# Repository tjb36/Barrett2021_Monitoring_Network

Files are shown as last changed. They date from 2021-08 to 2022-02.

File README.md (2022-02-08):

# "An Environmental Monitoring Network for Quantum Gas Experiments and Devices"

The purpose of this repository is to make available the data and code used in the study *"An Environmental Monitoring Network for Quantum Gas Experiments and Devices"*, by T. Barrett, et al. The publication is available [here](https://doi.org/10.1088/2058-9565/ac3385).

The system was designed for monitoring a suite of ultracold atom experiments, together with a variety of relevant environmental conditions to which the experiments are extremely sensitive. Approximately ~100 sensors are installed onto the network, and the data is consolidated into a standardised format in a time-series database. All data is available to inspect remotely for end users through custom dashboards. A high level schematic of the system looks like the following:



The code in this repository is organsied according to several main blocks in the system:

1) Environmental measurements are collected using various transducers (photodiodes, thermocouples, current sensors, etc). There are multiple of these "nodes" located around the buliding, connected to an isolated internal local area network using ethernet cables. These microcontrollers are usually Arduino-based, because they are small, cheap, and quick to set up and can be learned by any users in the lab with little programming experience. Examples of firmware deployed on these devices can be found at /Microprocessors Firmware/Sensor Node Devices/. Several transducers will typically be interfaced using the same microcontroller - for example, the board detailed at /Electronics/Photodiode and Thermocouple Amplifier/ allows x12 photodiodes and x8 thermocouples to be measured in succession by a single microcontroller node (gerbers/drill manufacture files are provided).

2) After a set time interval (typically every 20 seconds), a "Collector" microprocessor will poll all the node microcontrollers around the building, requesting that they take sensor readings and send back the values via the network. The firmware for this device can be found at /Microprocessors Firmware/Firmware_Collector.ino. This device keeps track of whether a reply was received from each device (to allow alerts to be sent out if a device becomes inactive), and sends the data as they arrive via serial USB connection to a "Parser" device, based on a Raspberry Pi.

3) The python script running on the Raspberry Pi can be found at /Parser Script/MapCollectorValuesToInfluxDB.py. The Raspberry Pi acts as the single points of contact with the outside internet, and the USB serial acts as a bridge between the internal LAN and the external internet (to avoid connecting many individual microcontrollers to the internet, and allow clearer separation). This script receives the data from the Collector via USB, performs a series of checks on the integrity of the data, and then extracts the relevant values from the payload. The script adds tags, and performs conversion from ADC counts to sensor values, for example (using calibration constants), and finally sends the data via HTTP to the InfluxDB database for storage.

4) An InfluxDB instance needs to be set up at a location that is accessible by the Raspberry Pi, and by default listens on port 8086. InfluxDB can be installed according to the developer's website https://portal.influxdata.com/downloads/ (a docker image is available to make installation quick and simple). In our setup, a virtual machine (VM) provisioned by the university hosts the InfluxDB instance, with 1TB of backed-up disk space (although the amount of data accumulated is typically only several GB per year).

5) For data visualisation, a Grafana instance must be set up, which can be done according the developer's website https://grafana.com/grafana/download?pg=get&plcmt=selfmanaged-box1-cta1 (similarly to InfluxDB, a docker image is available for easy installation). The Grafana instance must then be pointed to the InfluxDB location (in our setup, both Grafana and InfluxDB run on the same virtual machine). Custom dashboards should then be created in Grafana, and data be accessed by individual users as needed.

Typical examples of dashboards are shown below:

Dashboards

which are displayed on various screens around the labs:



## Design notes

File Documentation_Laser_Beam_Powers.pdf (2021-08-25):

## QSD Monitoring Network

## Measuring Laser Beam Powers

T. Barrett

July 2018

### Measuring Laser Beam Powers

Laser beam power is measured with a photodiode - a device which produces electron-hole pairs when photons of sufficient energy fall on the depletion region of the p-n junction semiconductor. Because there is a separation of charge either side of the depletion region, there is also an internal electric field across it. Therefore, when light falls on the active area the electrons move towards the cathode and holes towards the anode, leading the generation of an electrical photocurrent. To convert the photocurrent into a measurable voltage signal, a transimpedance amplifier can be used, shown schematically in Fig. 1.

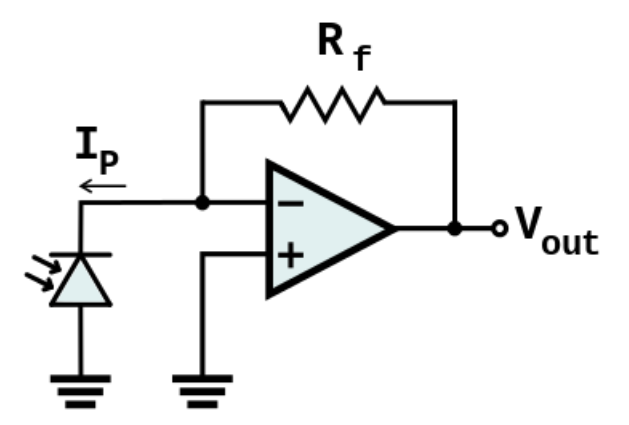
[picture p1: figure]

FIGURE 1: Schematic of a photodiode connected in photovoltaic mode with a transimpedance amplifier configuration, which gives an output voltage proportional to
the incident light power that can be scaled using the feedback resistor.

Photodiodes can be operated in either of two modes: photoconductive (with an external reverse bias applied across it), or photovoltaic (with zero bias across it). In general, photovoltaic mode reduces dark current, but is less optimal for bandwidth and response time. An excellent source of information on photodiode circuits and configurations is the book Photodiode Amplifiers - Op Amp Solutions, by J. Graeme [1]. In the particular application described in this document bandwidth is not a priority, and the photovoltaic arrangement is employed as shown in Fig. 1. Here, the op amp acts to make both its inputs equal to each other, which is zero volts due the non-inverting input being explicitly grounded. Since the photocurrent Ip is forced to flow through the feedback resistor Rf
, the voltage drop across this resistor is

∆V pVout 0q Ip -
Rf
, | (1)

and so the output voltage Vout is simply linear with the photocurrent. The amount of photocurrent generated is also linear with incident optical power through a factor known as the responsivity (measured in AW1
), and so this configuration provides a measurable output voltage that is linear with laser light power, which can be conveniently scaled by changing the gain of the transimpedance amplifier using the feedback resistor.
It was decided to use the Thorlabs FDS100, shown in Fig. 2 a), which is a standard silicon photodiode with a large active area of 13 mm²
, and costing £10 each. The responsivity at 780 nm
is 0.5 AW1
, as can be seen in Fig. 2 b). For the transimpedance op amp, the MCP604X series from Microchip is used, which is available with either one, two, or four op amps in a single chip. This is a low power op amp, designed for battery powered applications. It has a relatively low bandwidth, but this isn’t an

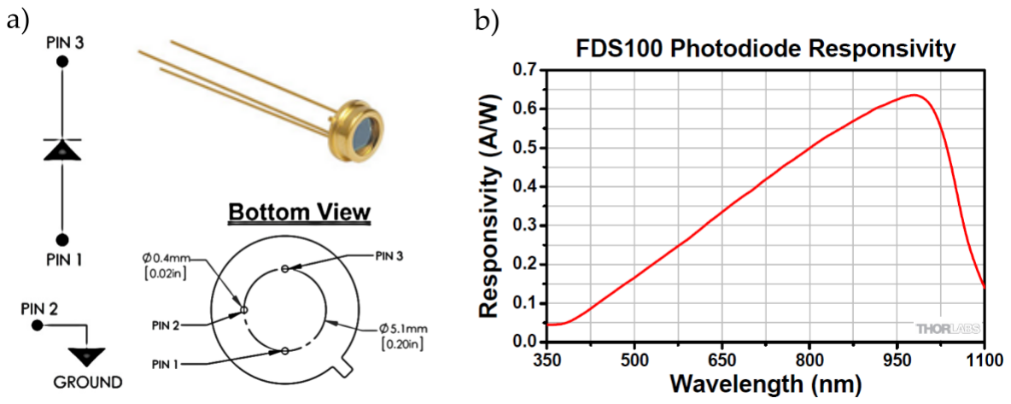
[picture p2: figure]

FIGURE 2: Thorlabs FDS100 Photodiode. a) Photograph and pin connections. b) Responsivity of the diode as a function of wavelength.

issue here. The main reason for using this op amp is that it is a single-supply rail-to-rail type, which means that its output voltage can get very close (to within 10 mV) of the power supply rails, in contrast to regular op amps which typically have a headroom of 1 V or more. This means that if the op amp is powered with 0 V (VSS) and +5 V (VDD), then its output signal will be able to get very close to +5 V, but not any higher. This is important because it provides a convenient way to protect the analog input pins of the Arduino microcontroller.
To be able to mount the FDS100 photodiodes and allow them to be integrated easily into the setup on the optical tables, several components were purchased from Thorlabs, as shown in Fig. 3. An 8 mm circular hole is drilled into the centre of a 1 inch SM1CP2 threaded cap, and the photodiode is then attached using a hot glue gun. This threaded cap then screws into a SMR1/M lens mount, which allows a neutral density filter to be attached if necessary (for example, NE01A-B. Everything can then be mounted to the optical table using standard posts. The photodiode is connected to wires using a removable socket with solder tail (STO5S).

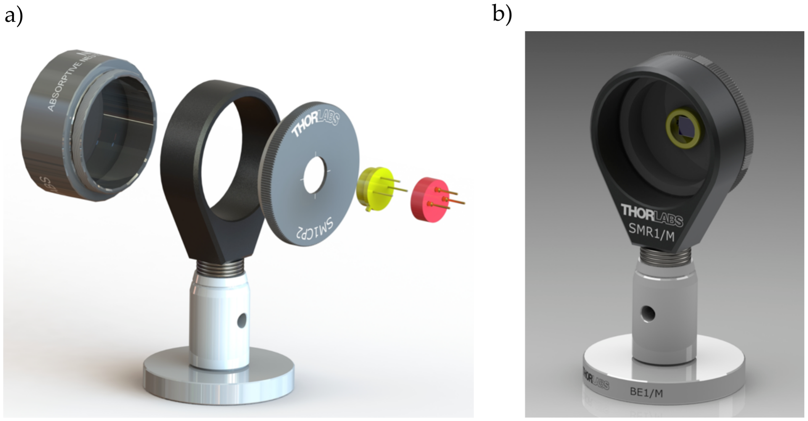
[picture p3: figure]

FIGURE 3: Exploded view a) and fully assembly b) photodiode with standard Thorlabs components.

For testing, the circuit was assembled and the output voltage was measured as a function of the incident laser light power, having a wavelength of 780 nm, with the results displayed in Fig.
4. Three different ranges with maximum powers of 100 µW, 1 mW, and 10 mW were achieved by inserting appropriate values of Rf
, and are shown in (a), (b), and (c), respectively. In this case, the op amp was powered with 0 VÑ+3.3 V. It can be seen that the output voltage is nicely linear with input light power, and never exceeds +3.3 V, meaning that the microcontroller will be safe.

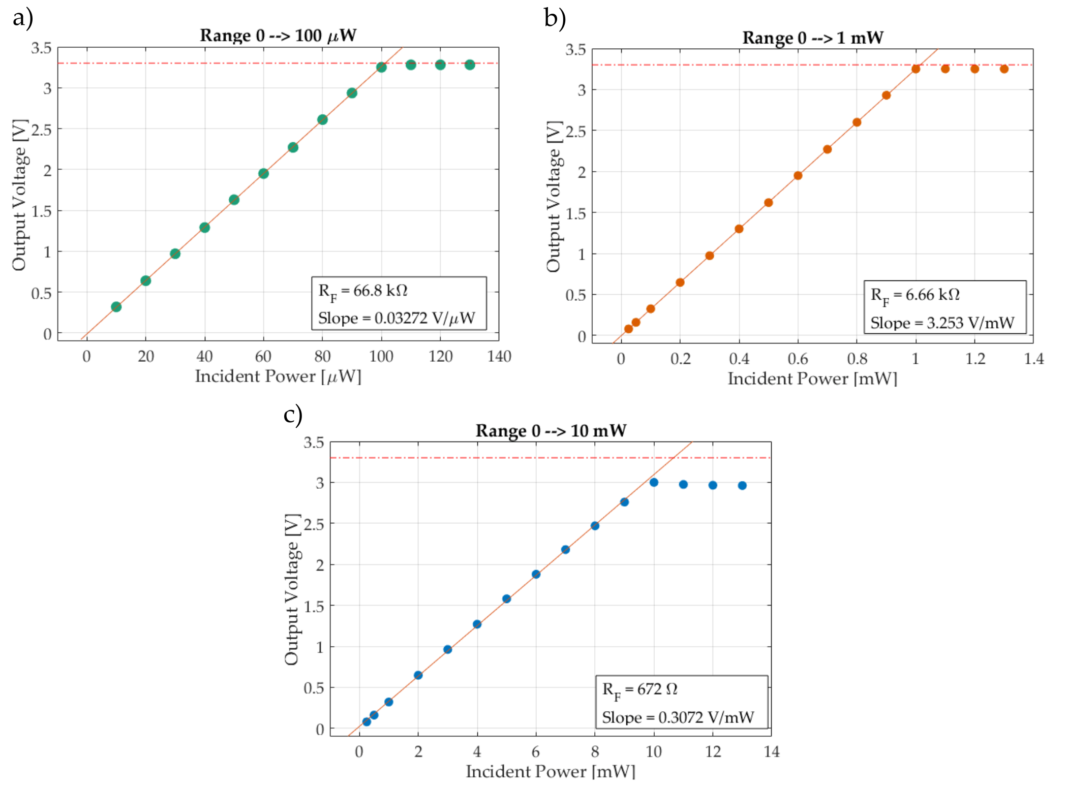
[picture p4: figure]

FIGURE 4: Measurements of the output voltage signal from a photodiode with a transimpedance amplifier as a function of incident laser light power. Three different ranges are shown in a), b) and c), corresponding to feedback resistors of 66.8 kΩ, 6.66 kΩ, and 672 Ω, respectively.

Arduino Code

The analog voltages can be read very easily using the following code, which reads x6 inputs. The ADC resolution is 10-bit on most Arduinos, giving possible values from 0 to 1023 as outputs from the analogRead() function.

1 /*

02 Mul tipleAnalogVol tageReadr
2 * Code f o r measuring mul tiple analog v ol t a g e s . 3 */
4
5 // Analog inpu t channel sen so r ADC v alue s
6 unsigned i n t sensorValueA0 = 0 ;
7 unsigned i n t sensorValueA1 = 0 ;
8 unsigned i n t sensorValueA2 = 0 ;
9 unsigned i n t sensorValueA3 = 0 ; 10 unsigned i n t sensorValueA4 = 0 ; 11 unsigned i n t sensorValueA5 = 0 ; 12 S t ri n g p aylo ad S t r ;
13
14 void se tup ( ) {
15 S e r i a l . begin ( 9 6 0 0 ) ; 16 }
17
18 void loop ( ) {
19
20 | sensorValueA0 = analogRead (A0 ) ;
21 | sensorValueA1 = analogRead (A1 ) ;
22 | sensorValueA2 = analogRead (A2 ) ;
23 | sensorValueA3 = analogRead (A3 ) ;
24 | sensorValueA4 = analogRead (A4 ) ;
25 | sensorValueA5 = analogRead (A5 ) ;
26 | p aylo ad S t r = ”” ;
27 | p aylo ad S t r = p aylo ad S t r + sensorValueA0 + ” , ” + sensorValueA1
28 | + ” , ” + sensorValueA2 + ” , ” + sensorValueA3 + ” , ”
29 | + sensorValueA4 + ” , ” + sensorValueA5 ;
30
31 | S e r i a l . p ri n t ( ”Analog Vol t age s : ” ) ;
32 | S e r i a l . p ri n tl n ( p aylo ad S t r ) ;
33 | delay ( 1 0 0 0 ) ;
34 }

The output from the Serial Monitor is shown in Fig. 5.

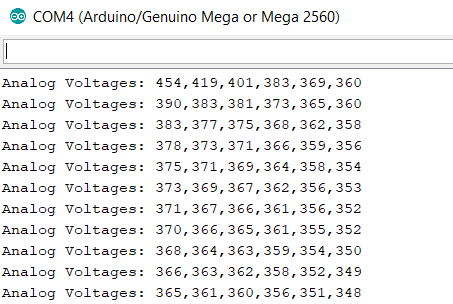
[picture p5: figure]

FIGURE 5: Serial Monitor output from reading multiple analog voltages.

### 1 References

[1] J. Graeme. Photodiode Amplifiers - Op Amp Solutions. McGraw-Hill Education, 1995.

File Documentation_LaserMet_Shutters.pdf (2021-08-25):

## QSD Monitoring Network

## Measuring LaserMet Shutter States

T. Barrett

July 2018

### Measuring LaserMet Shutter States

At the output of each of the 20 m seed fibres around the labs, as well as in front of every laser, is an LS10-12 LaserMet safety laser beam shutter, capable of blocking several watts of optical power. These shutters are connected to a safety interlock system, and when the interlock goes into a tripped state (for example, when lab door is left open for too long) the shutter power is removed and the flag falls down under gravity, blocking the beam. It is useful to be able to monitor the states of these shutters around the building, to know exactly where there is laser light present in the line at any one time.

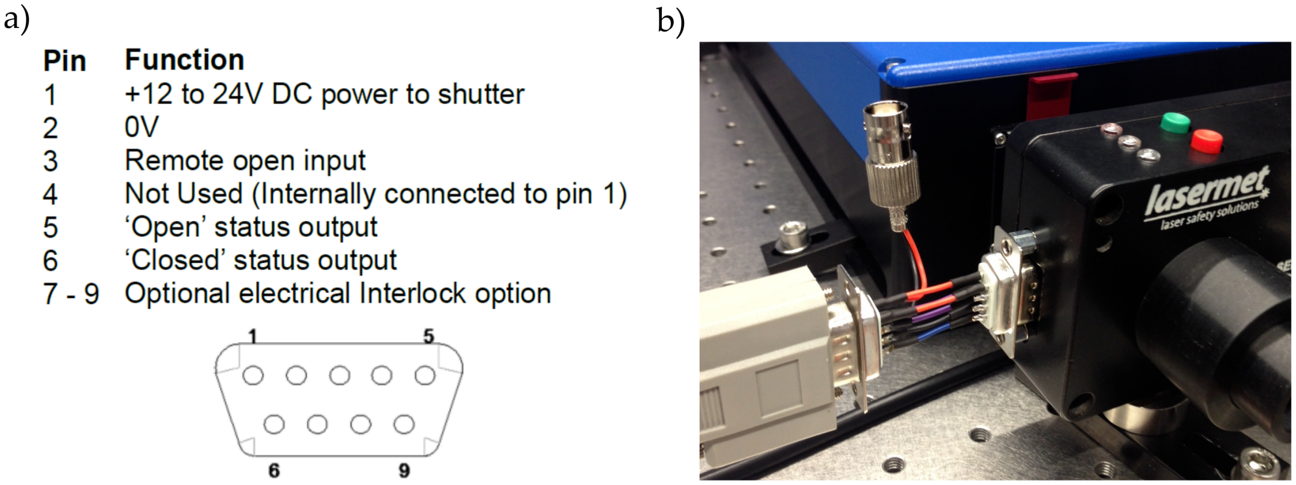
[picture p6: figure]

FIGURE 1: Remote monitoring of the LaserMet shutter states. a) Pin allocations for the 9-pin subD connector. b) An in-line adapter to connect the ’Open status output’
pin to an external device via BNC cable.

The shutter is mounted on the optical bench and interfaced with a 9-pin subD cable, as can be seen in Fig. 1 b). Page 3 of the LS10-12 user manual shows that there is a ’Open status output’ on pin 5 of the subD, with the pin allocations given in Fig. 1 a). When the shutter is opened (which is indicated by the red light on top of the shutter switching on), then the power supply of the system, which is +22 V in this case, is sent to pin 5. This signal allows remote monitoring of the shutter state.
In order to get access to this ’open status output’ pin, we made some adapters which go in-line with the shutter, connecting the centre pin of a BNC cable to pin 5, and the shield of a BNC to ground on pin 2. The adapter is shown after installation in Fig. 1 b). When the shutter is open, the centre pin of the BNC will get +22 V with respect to the outer shield. This allows access to the ’open’ indicator signal, whilst avoiding having to cut into the existing cable, and the adapter can simply be plugged in.
One problem is that the shutter ’open status’ pin receives +22 V, which is too high for the Arduino digital input pins, which are tolerant only up to +5 V on most models (and only to +3.3 V on the Due). Therefore, to convert the higher voltages into lower ones, an optocoupler circuit was designed, and is shown schematically in Fig. 2 a). The optocoupler used is the Vishay VO2630, which is a dual channel version - allowing two shutters to be interfaced with the same circuit. The datasheet states that a minimum of 5 mA is needed to turn on the input side LEDs, and so a 4 kΩ resistor is placed in series with the input from the shutter, to allow this current to flow. The output sides of the optocoupler then connect to two spare digital input pins on the Arduino microcontroller. The truth table in the VO2630 datasheet (page 3) shows that there is an inversion of the logic - i.e. when the input is high, the output is pulled low. Therefore, in the Arduino sketch, when an input LOW level is detected, this is interpreted as a ’shutter open’ signal, and vice versa. The 4 kΩ pull-up resistors on the output side ensure that the digital input pins remain HIGH when the shutters are closed and the optocoupler LEDs are off. This HIGH level voltage is now only +5 V, which is safe to pass to the microcontroller digital input pins. The whole circuit was made into a compact PCB, with two independent channels, a 3D view of which is shown in Fig. 2 b).

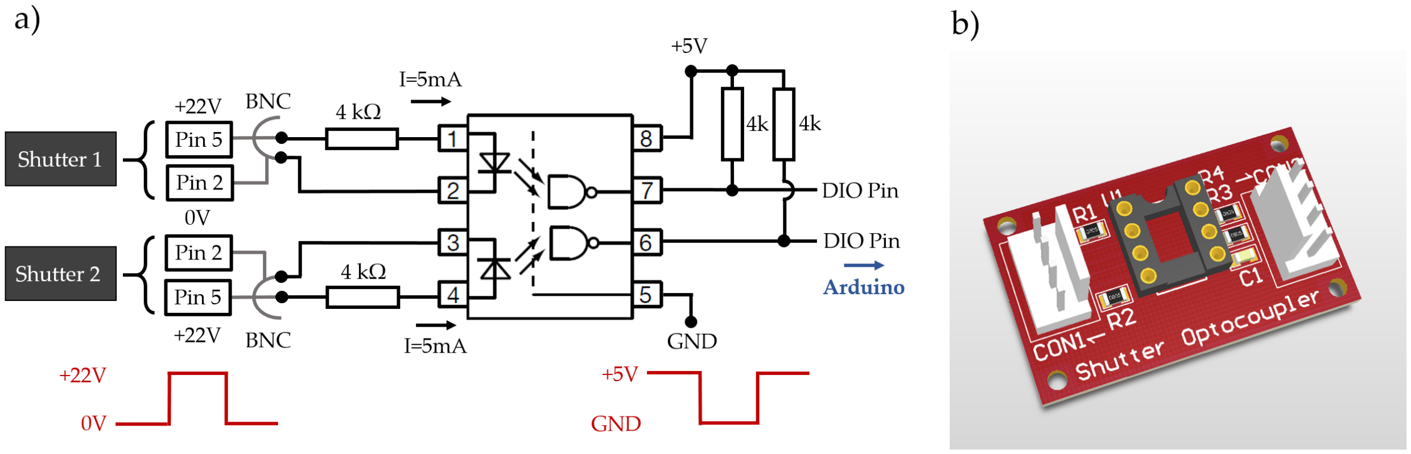
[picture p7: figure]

FIGURE 2: a) Schematic of the ’Shutter Optocoupler’ circuit. The circuit takes the +22 V signal output from the LaserMet shutters when they are open, and converts it down to +5 V, which can be safely read by an Arduino microcontroller’s digital input pins. b) A 3D view of the small PCB, made to facilitate two independent conversion channels, for two shutters in the lab.

Arduino Code

1 /*

04 L ase rMe tShu t te rRe ade r
2 | Code f o r reading in the s t a t e s o f two LaserMet s h u t t e r s
3
4 */
5
6 c on s t i n t Pi n S h u t t e r 1 = 2 ; 7 c on s t i n t Pi n S h u t t e r 2 = 3 ; 8 i n t S h u t t e r S t a t e 1 = 0 ;
9 i n t S h u t t e r S t a t e 2 = 0 ;
10
11 void se tup ( ) {
12
13 | S e r i a l . begin ( 9 6 0 0 ) ;
14 | pinMode ( Pi n S h u t t e r 1 , INPUT) ;
15 | pinMode ( Pi n S h u t t e r 2 , INPUT) ;
16
17 }
18
19 void loop ( ) {
20
21 | i f ( di gi t alR e a d ( Pi n S h u t t e r 1 ) == HIGH) {
22 | S h u t t e r S t a t e 1 = 0 ;
23 | } el s e {
24 | S h u t t e r S t a t e 1 = 1 ;
25 | }
26
27 | i f ( di gi t alR e a d ( Pi n S h u t t e r 2 ) == HIGH) {
28 | S h u t t e r S t a t e 2 = 0 ;
29 | } el s e {
30 | S h u t t e r S t a t e 2 = 1 ;
31 | }
32
33 | S e r i a l . p ri n t ( ” S h u t t e r 1 S t a t e = ” )
34 | S e r i a l . p ri n t ( S h u t t e r S t a t e 1 )
35 | S e r i a l . p ri n t ( ” , S h u t t e r 2 S t a t e = ” )
36 | S e r i a l . p ri n tl n ( S h u t t e r S t a t e 2 )
37
38 delay ( 1 0 0 0 )
39
40 }

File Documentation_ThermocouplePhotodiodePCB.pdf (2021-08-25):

# QSD Monitoring Network

# Multiple Thermocouple and Photodiode PCB

# T. Barrett

# July 2018

# Multiple Thermocouple and Photodiode PCB

In most cases, we will want to read in several thermocouples and photodiodes signals from different sources, all from the same microcontroller. For the temperatures, many of the MAX31855K

# breakout boards could be connected together. However, for a neater solution, custom PCBs

were designed and assembled, as in Fig. 1. Each PCB allows x12 photodiodes, and x8 thermocouples. The latter makes the board useful when performing a vacuum bakeout, for example, when many locations on the chamber need to be simultaneously measured.

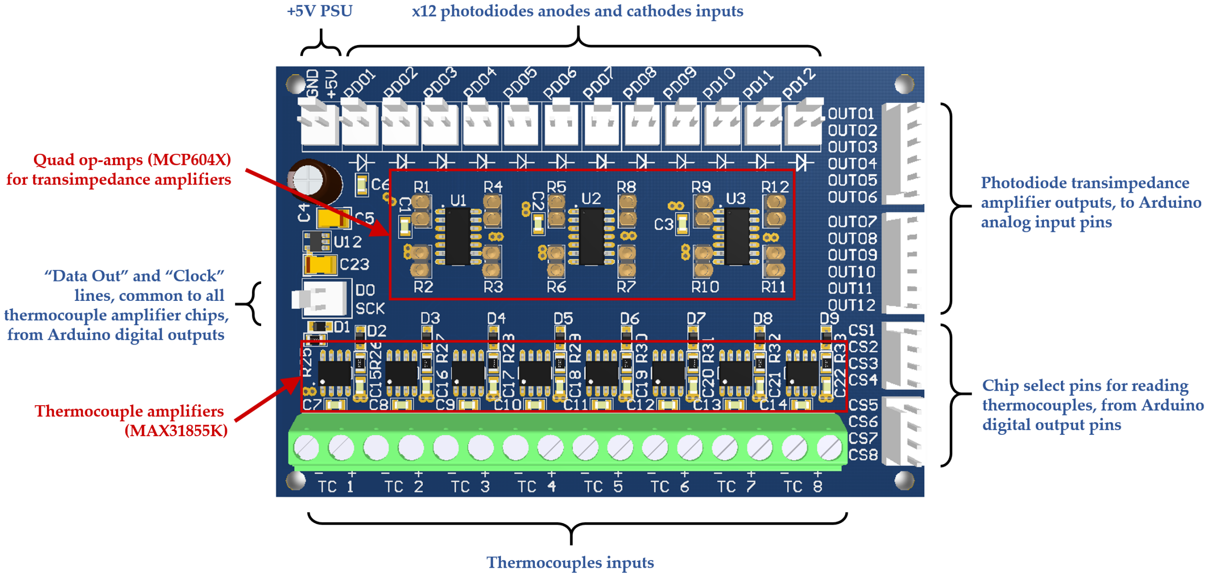
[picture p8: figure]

# FIGURE 1: PCB for reading multiple temperatures and laser powers. The board allows

x8 thermocouples and x12 photodiodes to be read.

# The design is based on the MAX31855K breakout board, and incorporates independent am-

plifier chips - one per thermocouple. However, there is only a single +3.3 V regulator (LP2981-
N) shared amongst all chips, along with a single set of decoupling power supply capacitors. All

# amplifiers also share common ’Data Out’ (DO) and ’Clock’ (SCK) lines, reducing the number

of digital output pins required. Each amplifier chip still requires its own dedicated ’Chip Se-lect’ (CS) pin, which indicates to each one that it’s time to read data. All thermocouple headers have 10nF capacitors across the terminals to reduce noise, as well as the digital pins having a resistor-diode combination to make the pins both 5 V and 3.3 V tolerant, for compatibility with different microcontrollers.
For the photodiodes, the PCB includes x3 MCP6044 op amps, which are quad versions,

# and therefore allows x12 photodiodes to be amplified. The op amps are configured in tran-

simpedance configuration, as described in the documentation Measuring Laser Beam Powers, and have sockets for through-hole axial resistors to be swapped out easily for changing the amplifier gains.

# Multiple Thermocouple and Photodiode PCB Schematics

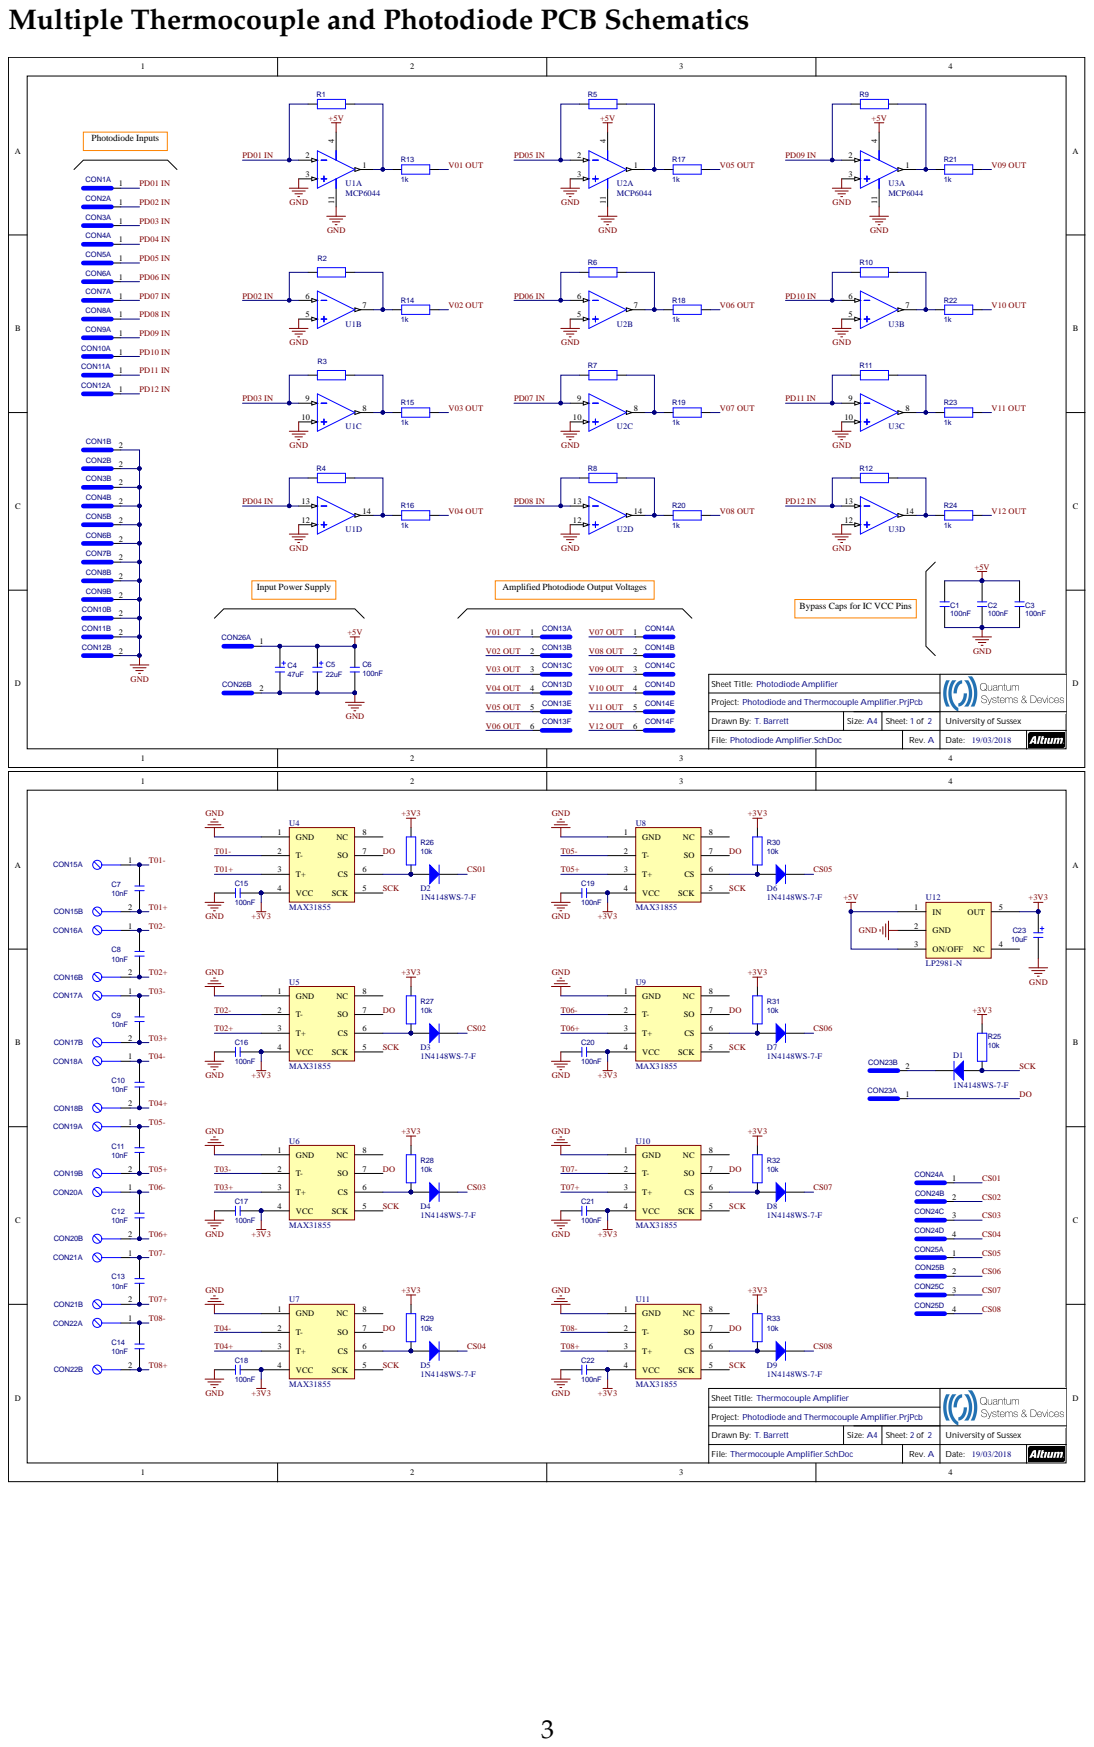
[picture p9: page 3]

Amplified Photodiode Output Voltages

Bypass Caps for IC VCC Pins

Project: Photodiode and Thermocouple Amplifier.PrjPcb

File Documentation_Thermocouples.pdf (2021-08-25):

## QSD Monitoring Network

## Measuring Temperatures

T. Barrett

July 2018

### Measuring Temperatures

For sensing temperatures in the lab, it was decided to use thermocouples, since they are cheap, reliable, and allow a high range of temperatures to measured. This means that the same system can be used when baking out a vacuum chamber, which typically means reaching temperatures of up to 200 C. Specifically, the most common thermocouple is the K-type, which has a range of around (200 C Ñ 1250 C).

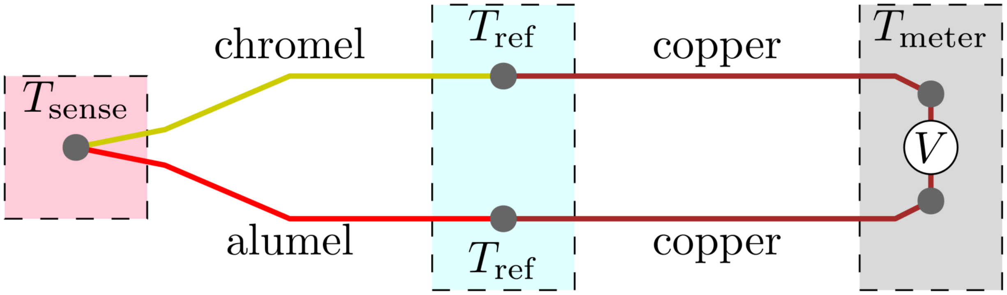
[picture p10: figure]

FIGURE 1: Schematic of a thermocouple. Two different metals are joined and positioned at the region to be sensed, Tsense. By knowing the temperature at the reference point, Tref, the absolute temperature can be determined by appropriate conversion of
the voltage, V . Image taken from [1]

A thermocouple, shown schematically in Fig. 1, relies on the Seebeck Effect, which describes the appearance of temperature-dependent voltage at the junction of two wires of different metals, converting thermal energy into electrical energy. For the K-type thermocouples, the positive lead is usually chromel (90% nickel, 10% chromium), and the negative lead alumel (95% nickel, 2% aluminium, 2% magnesium, 1% silicon). The voltage produced is very small (typically 1 mV at room temperature, with a sensitivity of 41 µV C

1
) and so must be amplified to a measurable value. In addition, the voltage must be linearised, along with being corrected for the cold-junction temperature. This is because the thermocouple is a differential device and so must be compensated with a reference junction of known temperature, in order to obtain an absolute value.

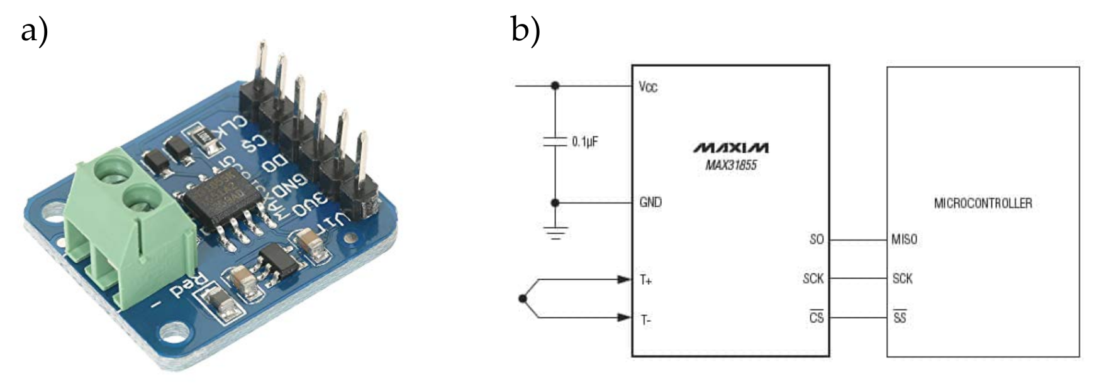
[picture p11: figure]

FIGURE 2: a) Adafruit MAX31855K assembled breakout board and b) connections schematic to the chip itself.

A convenient integrated circuit (IC) chip to use for this purpose is the MAX31855K from Maxim, which is optimised specifically for the K-type thermocouple, and whose schematic is shown in Fig. 2 b). This chip performs cold-junction compensation by measuring its internal temperature acting as a reference, in addition to the hot junction. Subsequently, the chip also converts the thermocouple voltage into a 14-bit digital signal ready for readout by using an on-board analog-to-digital converter (ADC), and so doesn’t require any analog inputs to work. The chip allows the temperature to be read out with a resolution of 0.25 C, and exhibits and accuracy of 2

C. Note in the datasheet that this IC has a typical conversion time of 70 ms, during which time the cold and hot junction voltages are converted, along with some fault detection being performed. In practice, this limits the frequency with which temperatures can be measured to 10 Hz, as one needs to wait at least until the conversion has finished before the next value can be read.
Communication with the IC (slave) is achieved using the serial peripheral interface (SPI) protocol, which requires connections to three digital I/O pins on an external microcontroller (master). The signals required are:
- SCK - serial clock - provides timing synchronisation between devices, and indicates when the next bit of data should be presented.
- SS (or CS) - slave select (or chip select) - typically pulled low by the master to indicate to the slave that it’s time to read data.
- MISO - master in slave out - contains each bit of data sent from the slave to the master.

The MAX31855K can be purchased already on a breakout board (for example, from Adafruit here: www.adafruit.com/product/269), which already has the necessary 3.3 V regulator for the power supply, along with level-shifting between 3.3 V and 5 V for the various communication lines. This breakout board is shown in Fig. 2 a).
To interface between an Arduino microcontroller and the MAX31855K chip, it is most simple to use the Adafruit MAX31855.h library, available here:

https://github.com/adafruit/Adafruit-MAX31855-library.

In order to use the library, it is required to declare three digital output pins in the sketch, for CLK, CS, and DO. Then a thermocouple object should be created using the command:

1 Adafruit MAX31855 thermocouple (CLK, CS , DO) ;

Finally, the temperature in celsius can be read from the newly created object using the following command:

1 T value = thermocouple . re adCel siu s ( ) ;

The CS pin allows multiple MAX31855K ICs to be connected to the same SPI bus (all using the same SCK and MISO pins), but with each having their own CS pins. Then, when a particular CS pin is pulled low, only the corresponding chip begins listening on the bus, and all others being high will ignore the master. A complete minimum working example (MWE) allowing the Arduino to read x6 thermocouples is shown in the section Arduino Code below, which requires x6 independent CS pins, along with a shared DO pin and a shared CLK pin. The output from the Arduino IDE Serial Monitor is shown in Fig. 3 a), displaying a string of comma-separated temperature values being received over the serial port once per second. The time evolution of these temperatures after being saved to an external text file is shown in Fig. 3 b).

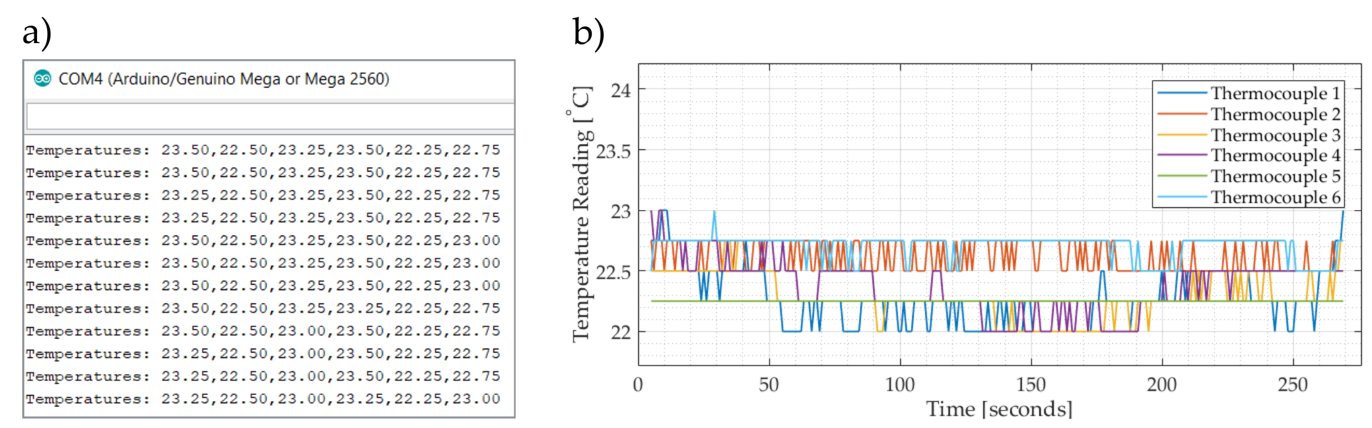
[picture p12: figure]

FIGURE 3: a) Six temperatures being received over the serial port, after being read from the MAX31855K ICs. b) Time evolution of received temperatures over several minutes.

Arduino Code

1 /*

01 MultipleThermocoupleRead
2 * Code f o r measuring mul tiple tempe r a tu res using MAX31855 chip s . 3 */
4
5 # include<SPI . h>
6 # in clude ”Adafruit MAX31855 . h”
7
8 # de fi ne DO 2 // Common MOSI pin
9 # de fi ne CLK 3 // Common s e r i a l cl o c k pin 10
11 // Chip s e l e c t pins
12 # de fi ne CS01 | 4
13 # de fi ne CS02 | 5
14 # de fi ne CS03 | 6
15 # de fi ne CS04 | 7
16 # de fi ne CS05 | 8
17 # de fi ne CS06 | 9
18
19 //THERMOCOUPLES
20 Adafruit MAX31855 thermocouple01 (CLK, CS01 , DO) ; 21 Adafruit MAX31855 thermocouple02 (CLK, CS02 , DO) ; 22 Adafruit MAX31855 thermocouple03 (CLK, CS03 , DO) ; 23 Adafruit MAX31855 thermocouple04 (CLK, CS04 , DO) ; 24 Adafruit MAX31855 thermocouple05 (CLK, CS05 , DO) ; 25 Adafruit MAX31855 thermocouple06 (CLK, CS06 , DO) ; 26 //
27
28 S t ri n g p aylo ad S t r ;
29 double temps [ 6 ] ; // B u f f e r to hold thermocouple da ta 30
31 void se tup ( ) {
32 S e r i a l . begin ( 9 6 0 0 ) ;
33 }
34
35 void loop ( ) {
36
37 | // Read thermocouples
38 | temps [ 0 ] = thermocouple01 . re adCel siu s ( ) ;
39 | temps [ 1 ] = thermocouple02 . re adCel siu s ( ) ;
40 | temps [ 2 ] = thermocouple03 . re adCel siu s ( ) ;
41 | temps [ 3 ] = thermocouple04 . re adCel siu s ( ) ;
42 | temps [ 4 ] = thermocouple05 . re adCel siu s ( ) ;
43 | temps [ 5 ] = thermocouple06 . re adCel siu s ( ) ;
44
45 | // Cons t ruc t s t r i n g to p rin t , using ” 0 . 0 ” i f NaN i s re tu rned
46 | p aylo ad S t r = ”” ;
47 | f o r ( i n t i = 0 ; i < 6 ; i ++) {
48 | i f ( isn an ( temps [ i ] ) ) {
49 | p aylo ad S t r = p aylo ad S t r + ” , ” + ” 0 . 0 ” ;
50 | } el s e {
51 | p aylo ad S t r = p aylo ad S t r + ” , ” + temps [ i ] ;
52 | }
53 | }
54
55 | S e r i a l . p ri n t ( ”Temperatures : ” ) ;
56 | S e r i a l . p ri n tl n ( p aylo ad S t r ) ;
57
58 delay ( 1 0 0 0 ) ;
59
60 }

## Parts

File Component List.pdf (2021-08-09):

Part Name / Model | Description
Arduino Nano | Collector Device (requests data from sensor node devices)
Raspberry Pi 3B | Parser Device (process and push data to InfluxDB)
Arduino Uno | Sensor Node Device (connect to sensor and take values)
Arduino Due | Sensor Node Device (connect to sensor and take values)
Arduino Nano | Sensor Node Device (connect to sensor and take values)
Freetronics Etherten | Sensor Node Device (connect to sensor and take values)
Freetronics DOG | Watchdog Timer Reset Module
Mini W5100 | SPI ethernet adapter module
HP JL256A Aruba 2930F | 48 port managed ethernet switch
Maxim MAX31855K | Thermocouple to digital converter
K-Type Thermocouple | Temperature and bakeout monitoring
Thorlabs FDS100 | Silicon photodiode for laser power monitoring
Microchip MCP6044 | Low voltage single supply quad op amp for transimpedence amplifiers
Thorlabs SM1CP2 | Parts to conveniently mount photodiodes to optical table
Thorlabs SMR1/M | Parts to conveniently mount photodiodes to optical table
Thorlabs NE01A-B | Parts to conveniently mount photodiodes to optical table
Thorlabs STO5S | Parts to conveniently mount photodiodes to optical table
Agilent UHV-24P | Ionisation gauge for detecting vacuum pressure
Agilent XGS-600 | Ionisation gauge controller
MAX3232 | RS232 serial to TTL level converter for communication with vacuum gauge
SP3232 | RS232 serial to TTL level converter for communication with vacuum gauge
LaserMet LS10-12 | High power laser safety interlock shutter
Vishay VO2630 | Optocoupler for interfacing with laser shutter
DRV425EM | Fluxgate magnetic field sensor for background field monitoring
DHT22 | Basic temperature and humidity sensor
BME280 | Basic temperature, humidity, and air pressure sensor
XF-936-FAR | RTD PT100 platinum high accuracy temperature probe
MAX31865 | PT100 amplifier and digital converter
CASR6 | 6A fluxgate-based electrical current transducer
CASR15 | 15A fluxgate-based electrical current transducer
CASR50 | 50A fluxgate-based electrical current transducer
SSD1306 | I2C OLED displays
OZ Optics OPM-11-780 | Optical fibres with 1% optical tap and photodiode for power monitoring

# Monitoring Network Components List

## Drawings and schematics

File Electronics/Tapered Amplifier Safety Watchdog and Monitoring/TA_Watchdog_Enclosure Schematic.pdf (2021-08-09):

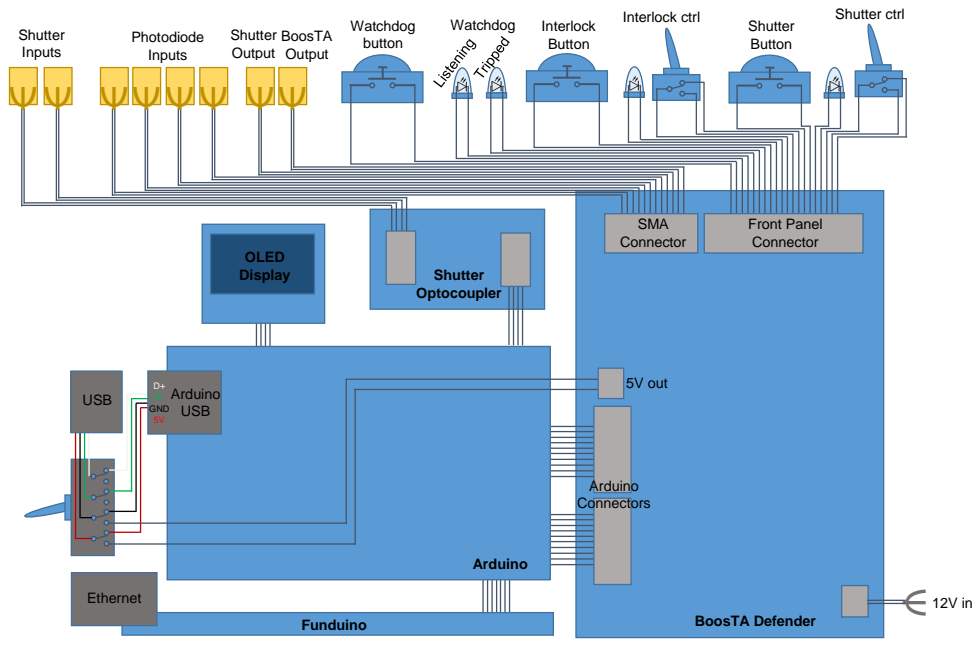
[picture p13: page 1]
Funduino; Shutter Optocoupler; Shutter Inputs; Photodiode Inputs; Watchdog button; Watchdog; Interlock; Button; Interlock ctrl; Shutter Output; BoosTA Output; Shutter Button; Shutter ctrl; BoosTA Defender; Front Panel Connector; SMA Connector; Arduino Connectors; 5V out; Arduino; OLED Display; USB; Ethernet; D+ D- GND 5V; Arduino USB

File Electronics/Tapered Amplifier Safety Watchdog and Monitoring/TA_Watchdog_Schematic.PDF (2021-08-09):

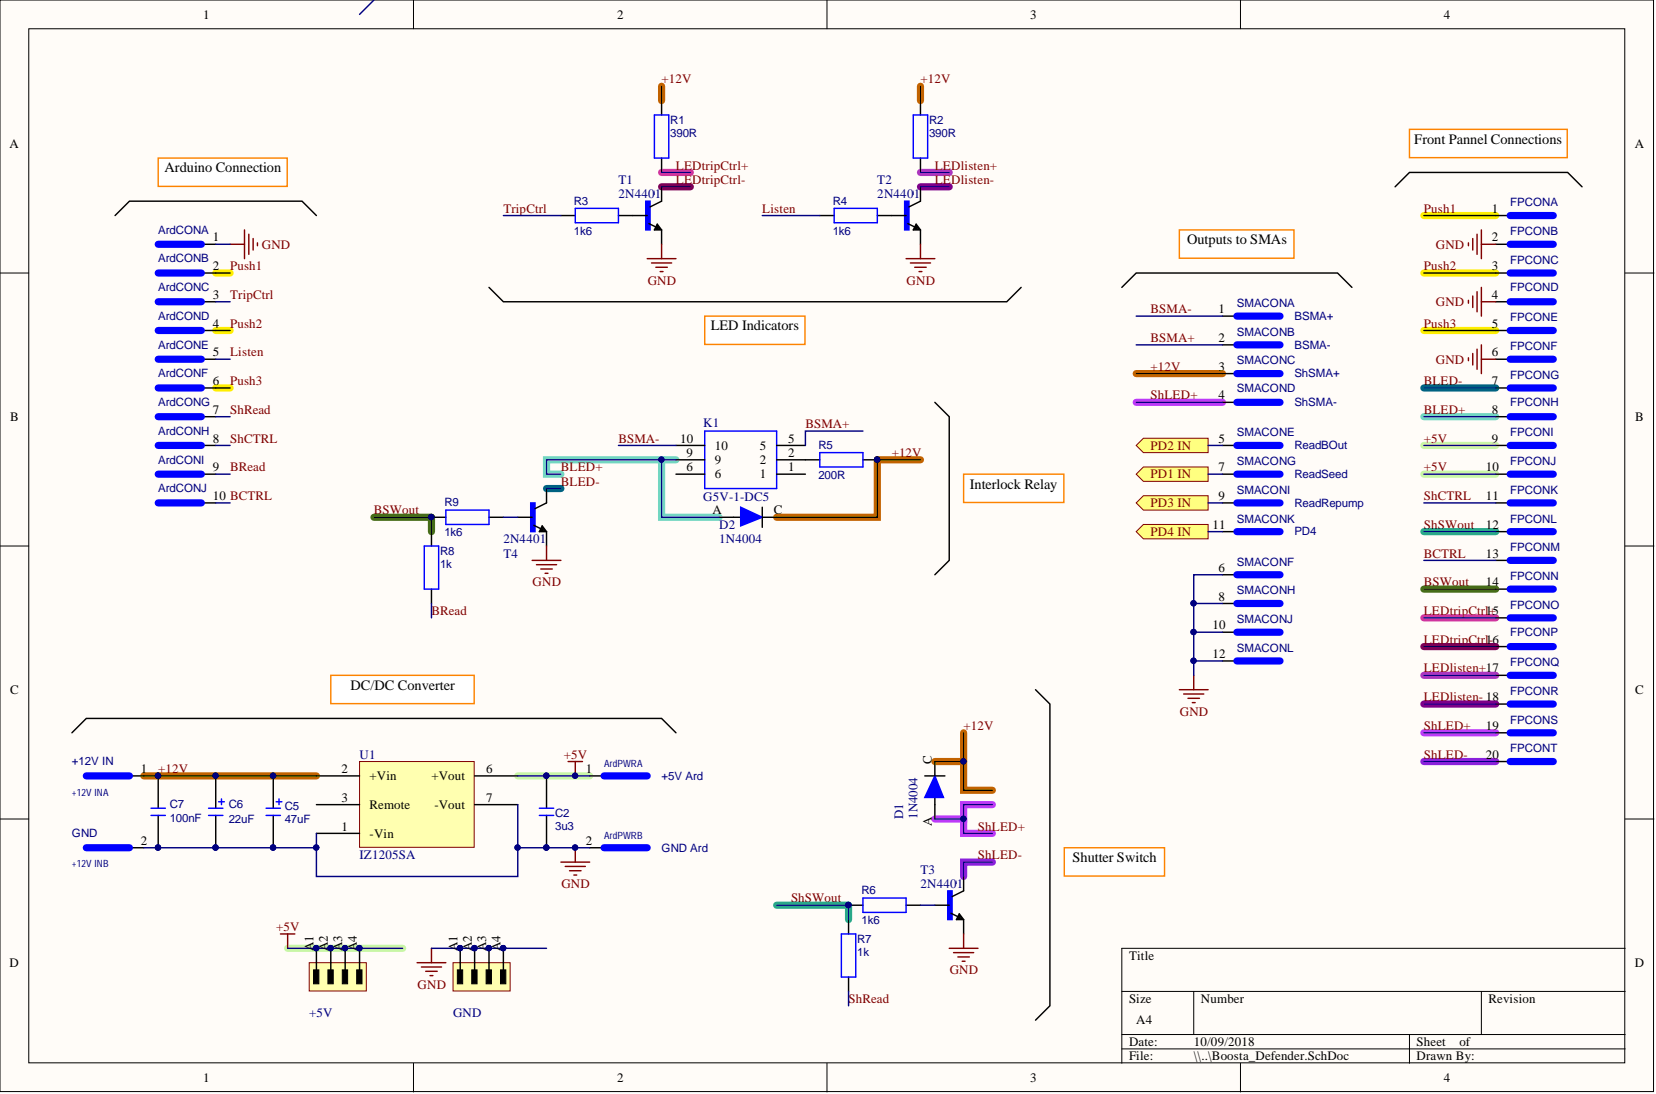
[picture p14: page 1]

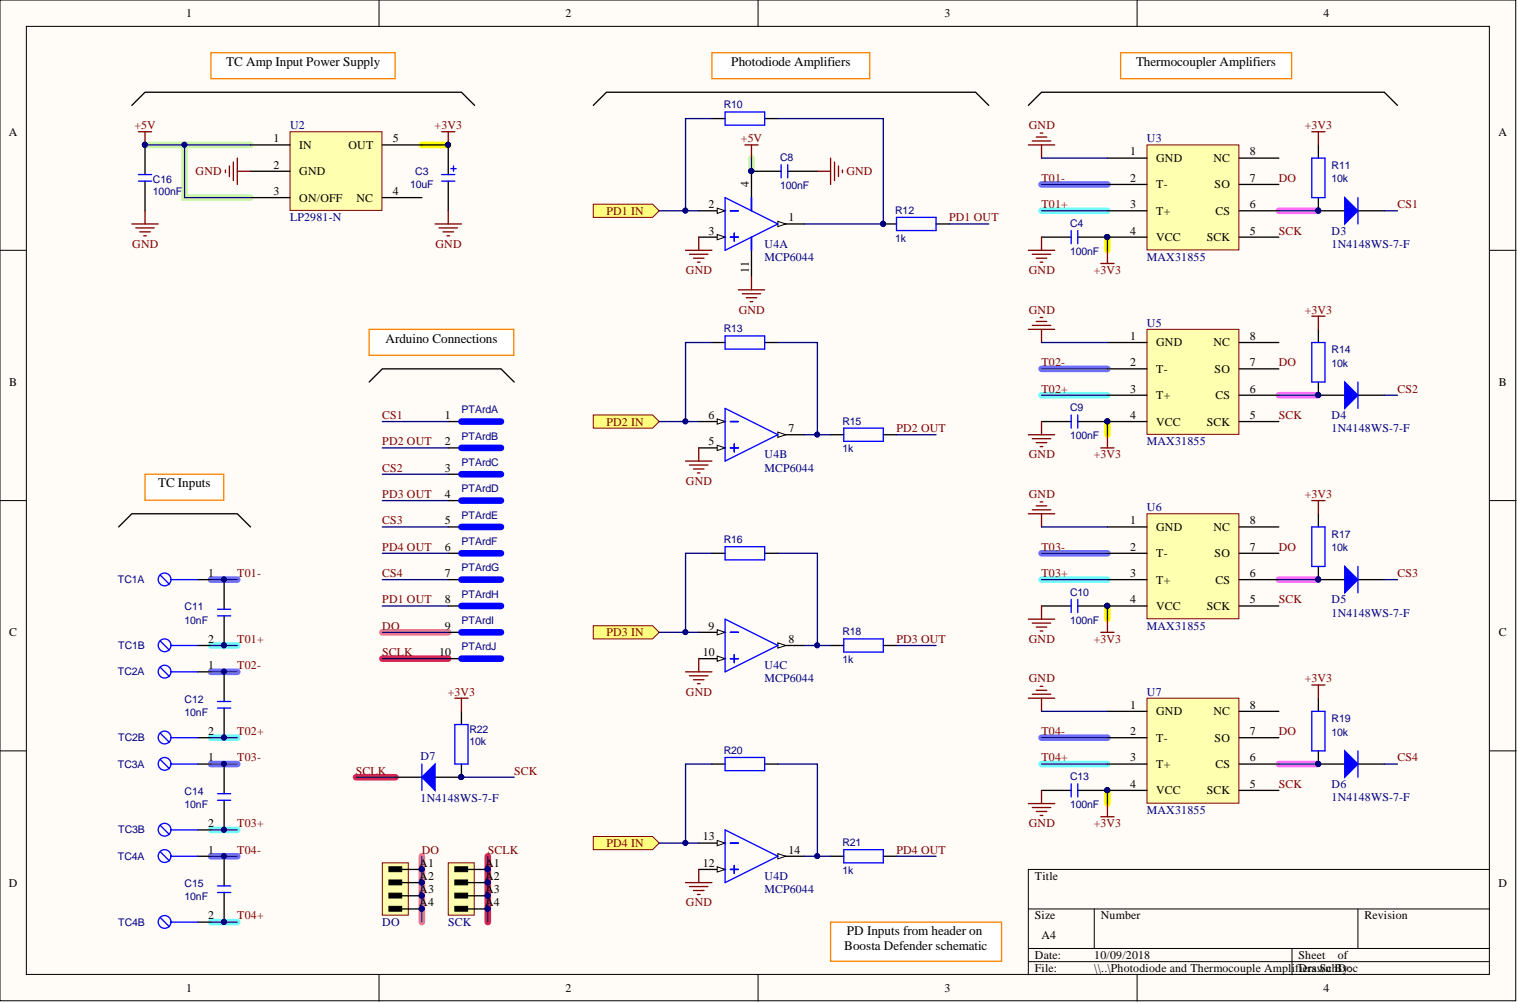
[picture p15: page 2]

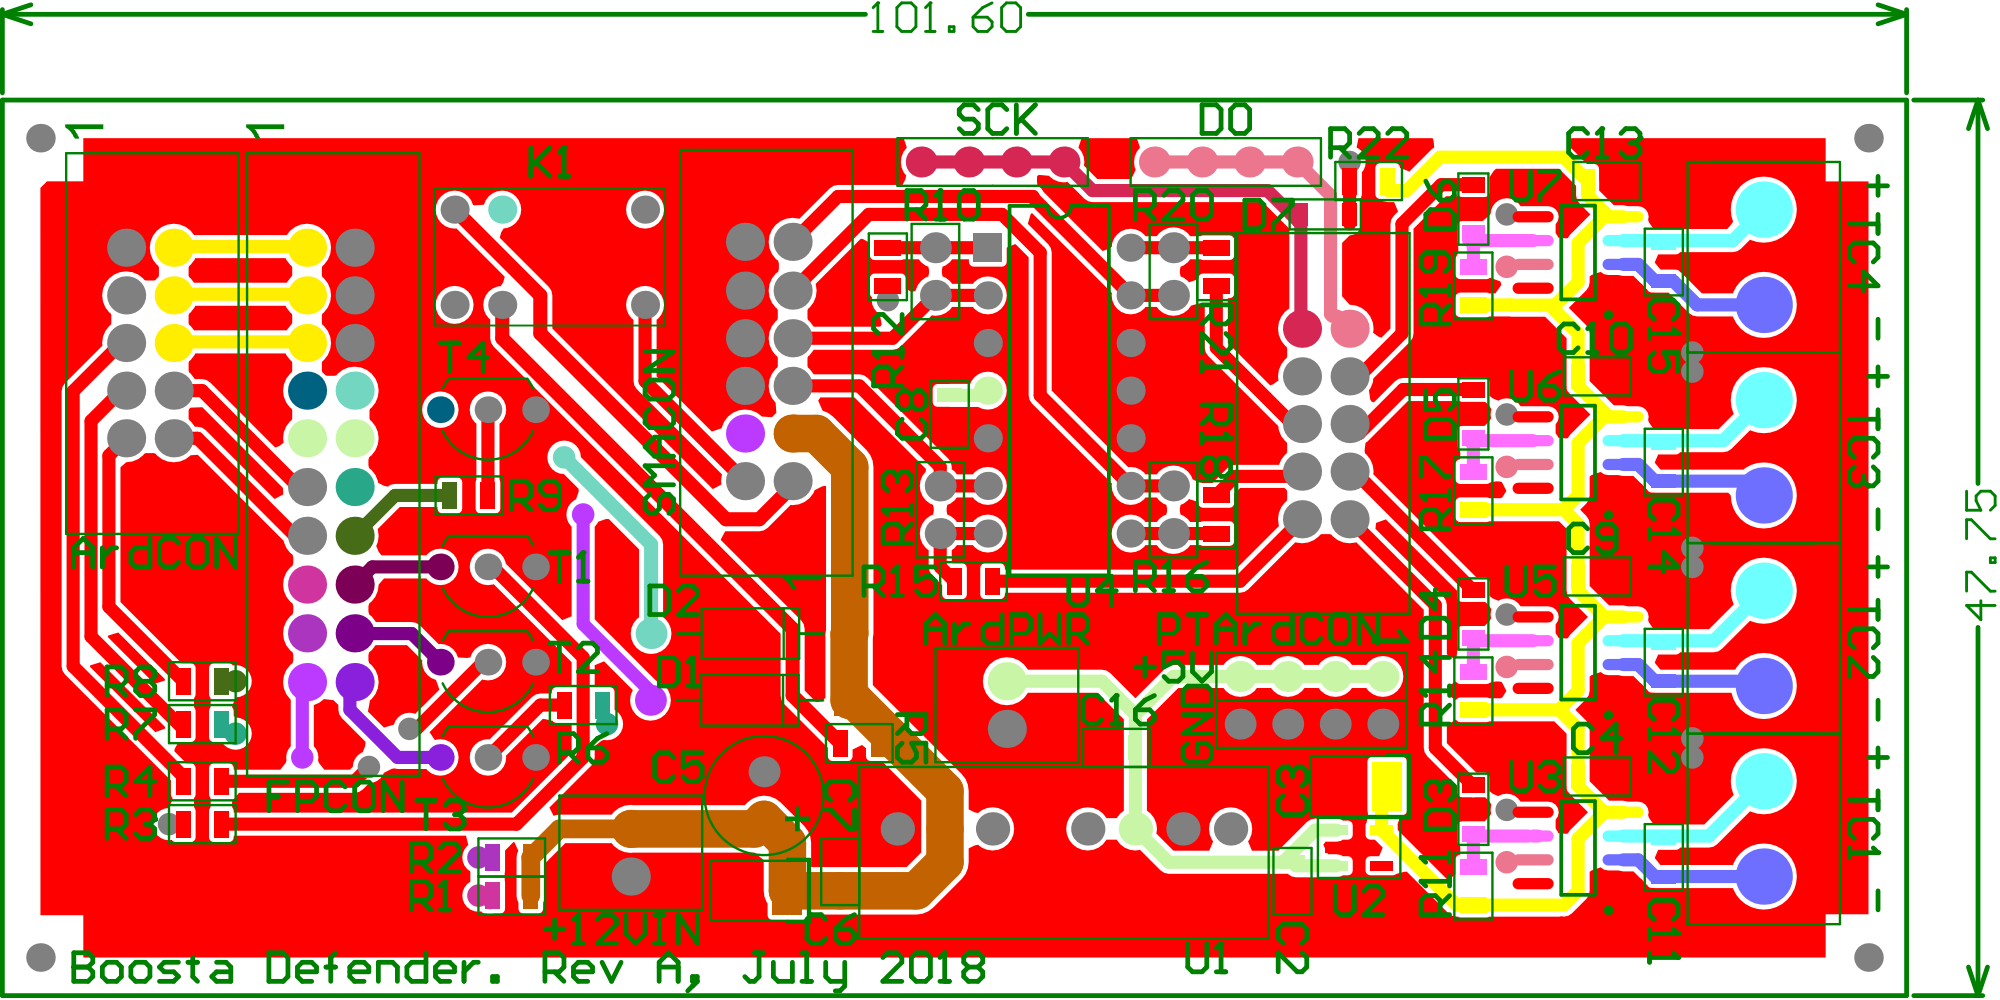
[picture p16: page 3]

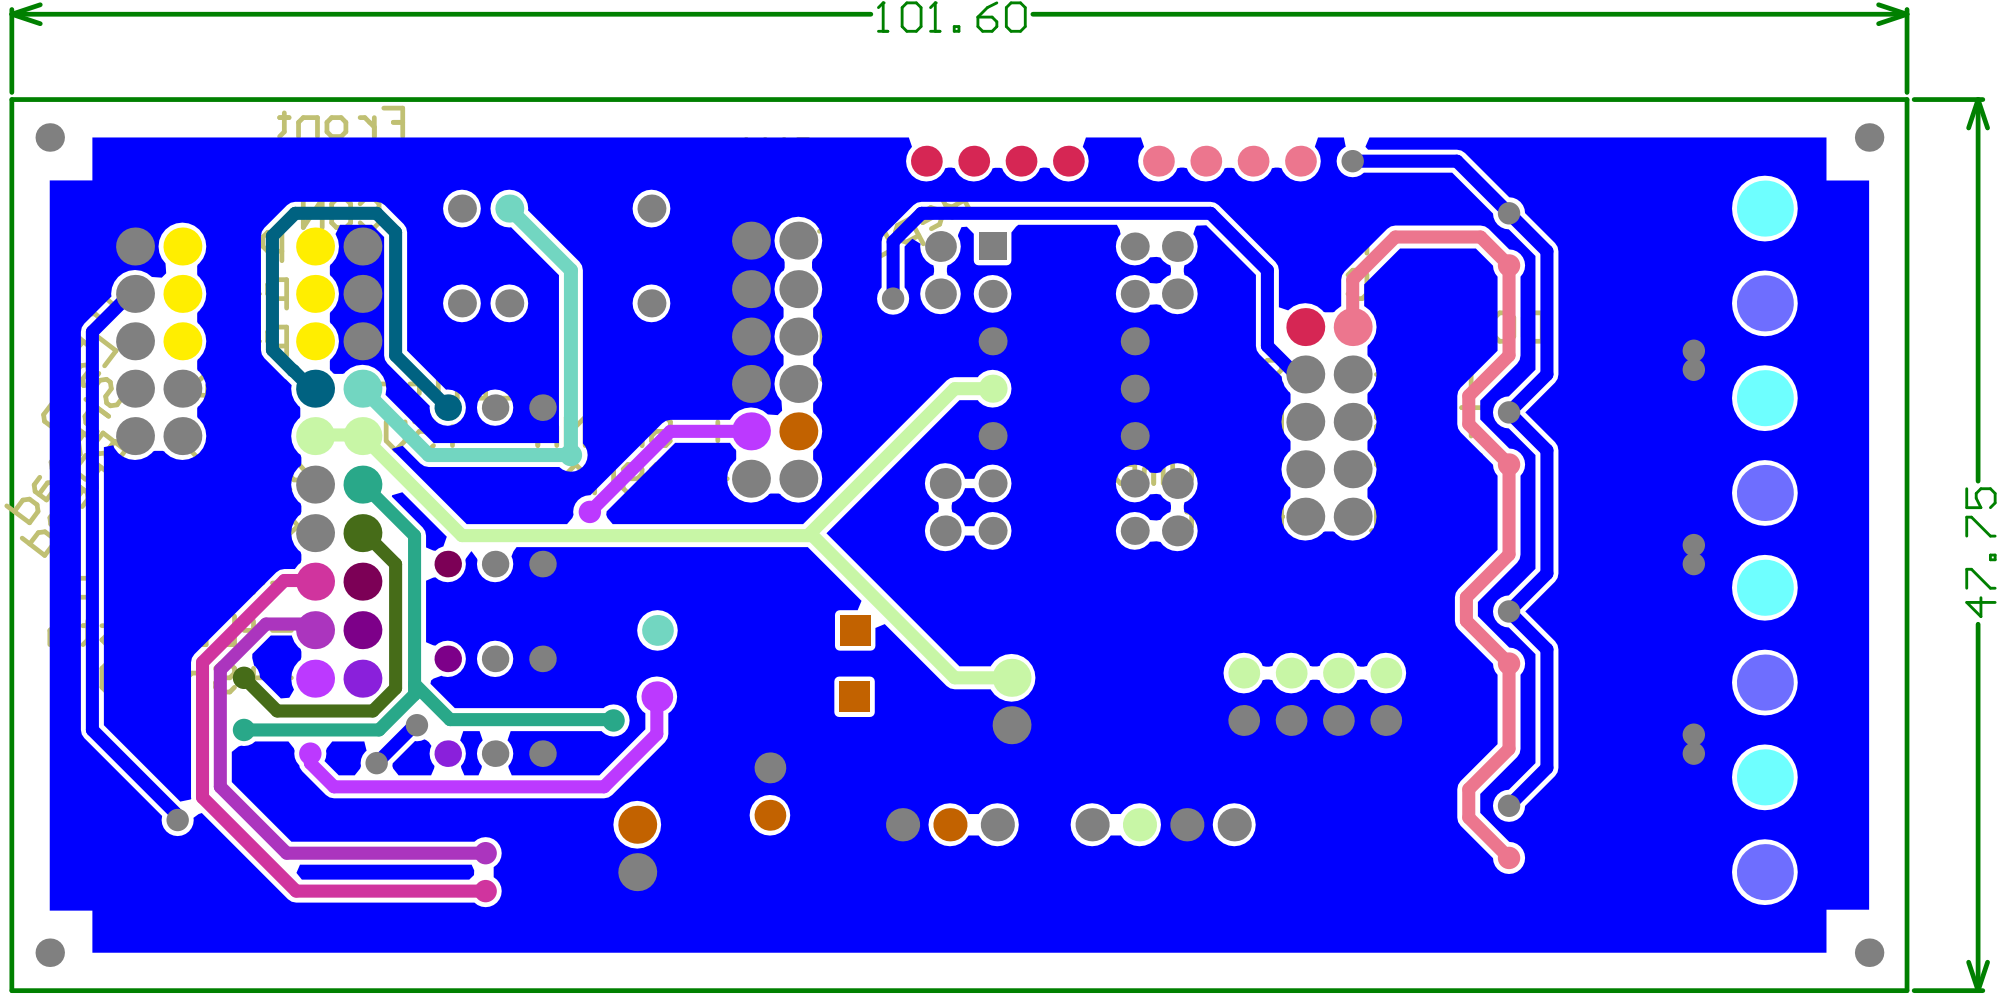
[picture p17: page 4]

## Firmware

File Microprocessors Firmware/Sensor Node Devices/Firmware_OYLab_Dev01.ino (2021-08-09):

#include <SPI.h>
#include <Ethernet.h>
#include<EthernetUdp.h>
#include "Adafruit_MAX31855.h"
//Needed for OLED
#include <Adafruit_SSD1306.h>
#include <Adafruit_GFX.h>

// OLED display TWI address /////////////////////////////////////////////////////////////////////////
#define OLED_ADDR   0x3C
// reset pin not used on 4-pin OLED module
Adafruit_SSD1306 display(-1);  // -1 = no reset pin
///////////////////////////////////////////////////////////////////////////////////////////////////////////

// Initialise Ethernet Parameters /////////////////////////////////////////////////////////////////////////
#define UDP_TX_PACKET_MAX_SIZE 150 //increase UDP size
EthernetUDP Udp;
byte mac[] = { 0xDE, 0xAD, 0xBE, 0xEF, 0xFE, 0xAD };
const unsigned int localPort = 1396;
IPAddress IP_Collector(169, 254, 128, 105);
IPAddress IP_OYLab_Dev01(169, 254, 128, 115);
char recvdBuffer[10];
int recvdPacketSize;
unsigned long ethLastRecvd = 0;
unsigned long ethTimeout = 40000;
///////////////////////////////////////////////////////////////////////////////////////////////////////////

// Thermocouple Variables ////////////////////////////////////////////////////////////////////////////////
#define DO  2 // Common MOSI pin
#define CLK 3 // Common serial clock pin
#define CS01  4 // Chip select pins
#define CS02  5
#define CS03  6
#define CS04  7

//THERMOCOUPLES
Adafruit_MAX31855 thermocouple01(CLK, CS01, DO);
Adafruit_MAX31855 thermocouple02(CLK, CS02, DO);
Adafruit_MAX31855 thermocouple03(CLK, CS03, DO);
Adafruit_MAX31855 thermocouple04(CLK, CS04, DO);



// DEFINE PINS /////////////////////////////////////////////////////////////////////////////////////////
int SeedOutput_Read = A3; // Analog input channel sensor ADC values
int PD4Output_Read = A2;
int RepumpOutput_Read = A1;
int BoosTAOutput_Read = A0;

int ShutterButtonPin = 46;
int ShutterPin = 41;
int ShutterPin_Read = 40;

int InterlockButtonPin = 42;
int InterlockPin = 39;
int InterlockPin_Read = 38;

int WatchdogButtonPin = 43;
int WatchdogPin = 44;
int WatchdogTripPin_Read = 45;

int LasermetShutterPin_Read = 34;
int RepumpShutterPin_Read = 35;

// Initialise Variables ///////////////////////////////////////////////////////////////////////////////////
String headerStr = "OYLab,Dev01";
String payloadStr;

double temps [4]; // Buffer to hold thermocouple data

int BoosTAOutputVal = 0;
int RepumpOutputVal = 0;
int PD4OutputVal = 0;
int seedOutputVal = 0;

const unsigned int delayTime = 0;
const float seedPowerThresholdLower = 15;
const float seedPowerThresholdUpper = 35;
float seedPower;
float BoosTAPower;
float RepumpPower;
float PD4Power;

bool watchdogTripped = false;

// Debounce Stuff ///////////////////////////////////////////////////////////////////////
const int buttons = 3; // number of buttons you use
const int ShuttersInterlocks = 4; // number of shutters and interlocks

int currState[ShuttersInterlocks] = {0};                  // both current state and state are needed for
int state[buttons] = {1};                                 // interlock and shutter because there are switches
int buttonState[buttons] = {1};                           // external to ard control that effect these states
int lastButtonState[buttons] = {1};
int buttonPin[buttons];
unsigned long lastDebounceTime[buttons] = {0};
/////////////////////////////////////////////////////////////////////////////////////////

// Display Screen Variables /////////////////////////////////////////////////////////////
const unsigned long screenUpdateInterval = 1000; // How often to take a data sample in ms
unsigned long previousScreenUpdateMillis = 0; // Time at which previous sample was acquired
unsigned long currentMillis = 0; // Current time elapsed since program started in ms
/////////////////////////////////////////////////////////////////////////////////////////

void setup() {

  // initialize and clear display
  display.begin(SSD1306_SWITCHCAPVCC, OLED_ADDR);
  display.clearDisplay();
  display.display();
  display.setTextSize(1);
  display.setTextColor(WHITE, BLACK);
  //display.dim(true);

  // Allow ethernet chip time to initialise after being powered up
  delay(1000);
  Serial.begin(57600);

  pinMode(53, OUTPUT); // Needed for slave select SPI for Mega (not connected)
  pinMode(10, OUTPUT); // SPI SS pin for most Arduino models (need to connect)

  pinMode(ShutterButtonPin, INPUT_PULLUP);
  pinMode(InterlockButtonPin, INPUT_PULLUP);
  pinMode(WatchdogButtonPin, INPUT_PULLUP);

  pinMode(ShutterPin, OUTPUT);
  pinMode(InterlockPin, OUTPUT);
  pinMode(WatchdogTripPin_Read, OUTPUT);

  Ethernet.begin(mac, IP_OYLab_Dev01);
  Udp.begin(localPort);
  delay(1000); // Allow ethernet chip time to initialise
  textDisplay("Ethernet initialisation started");


}

void loop() {

  currentMillis = millis();

  // READ PHOTODIODE POWERS /////////////////////////////////////////////////////////////
  seedPower = 0.0;
  BoosTAPower = 0.0;
  RepumpPower = 0.0;
  
  seedOutputVal = analogRead(SeedOutput_Read);
  seedPower = (seedOutputVal) / 1.0;
  BoosTAOutputVal = analogRead(BoosTAOutput_Read);
  BoosTAPower = (BoosTAOutputVal) / 752.0 *2680.0 ;
  RepumpOutputVal = analogRead(RepumpOutput_Read);
  RepumpPower = (RepumpOutputVal) / 706.0 * 61.0;
  
  PD4OutputVal = analogRead(PD4Output_Read);
  PD4Power = (PD4OutputVal) / 1023.0 * 1.0;
  ///////////////////////////////////////////////////////////////////////////////////////

  // DETECT STATE CHANGE OF DCHP INTERLOCK BUTTON ///////////////
  // DETECT STATE CHANGE OF WATCHDOG LISTENING BUTTON ///////////
  // READ LASERMET SHUTTER STATE ////////////////////////////////
  // READ FIBRE DOCK SHUTTER STATE //////////////////////////////
  // READ DCHP INTERLOCK STATE //////////////////////////////////
  // READ BOOSTA OUTPUT POWER ///////////////////////////////////
  // READ REPUMP POWER //////////////////////////////////////////


  // DEFINE REFERENCES ///////////////////////////////////////////////////////////
  int Shutter = 0;
  int Interlock = 1;
  int Watchdog = 2;
  int LasermetShutter = 2;
  int RepumpShutter = 3;

  buttonPin[Shutter] = ShutterButtonPin;
  buttonPin[Interlock] = InterlockButtonPin;
  buttonPin[Watchdog] = WatchdogButtonPin;
  ////////////////////////////////////////////////////////////////////////////////////////

  // CHECK BUTTON STATES /////////////////////////////////////////////////////////////////
  if (!watchdogTripped) {
    if (buttonStateChange(Shutter)) {
      Serial.println("Shutter State Changed");
      digitalWrite(ShutterPin, state[Shutter]);
    }

    if (buttonStateChange(Interlock)) {
      Serial.println("Interlock State Changed");
      digitalWrite(InterlockPin, state[Interlock]);
    }
  }

  if (buttonStateChange(Watchdog)) {
    Serial.println("Watchdog State Changed");
    digitalWrite(WatchdogPin, state[Watchdog]);
    if (watchdogTripped) { // resets the watchdog
      watchdogTripped = false;
      digitalWrite(WatchdogTripPin_Read, LOW);
    }
  }

  currState[Shutter] = digitalRead(ShutterPin_Read);
  currState[Interlock] = digitalRead(InterlockPin_Read);

  // Account for the fact that the optocoupler circuit has inversion
  if (digitalRead(LasermetShutterPin_Read) == HIGH) {
    currState[LasermetShutter] = 0;
  } else {
    currState[LasermetShutter] = 1;
  }

  if (digitalRead(RepumpShutterPin_Read) == HIGH) {
    currState[RepumpShutter] = 0;
  } else {
    currState[RepumpShutter] = 1;
  }

  ///////////////////////////////////////////////////////////////////////////////////////

  // WATCHDOG CONDITIONS ////////////////////////////////////////////////////////////////
  if (state[Watchdog]) {

    // Trip conditions: fibre dock shutter open AND seed power too low
    //               OR fibre dock shutter open AND seed power too high
    //               OR fibre dock shutter open AND DCHP controller interlock disabled

    //               OR BoosTA current applied AND fibre dock shutter closed
    //               OR BoosTA current applied and seed power too low


    if (((currState[Shutter] == 1) && (seedPower < seedPowerThresholdLower)) ||
        ((currState[Shutter] == 1) && (seedPower > seedPowerThresholdUpper))) {
      Serial.println("WARNING: Trip condition met");
      digitalWrite(WatchdogTripPin_Read, HIGH);
      watchdogTripped = true;
      digitalWrite(ShutterPin, LOW);
      state[Shutter] = 0;
      digitalWrite(InterlockPin, LOW);
      state[Interlock] = 0;
      digitalWrite(WatchdogPin, LOW);
      state[Watchdog] = 0;
    }

  }
  ///////////////////////////////////////////////////////////////////////////////////////

  // ETHERNET /////////////////////////////////////////////////////////////////////////////
  recvdPacketSize = Udp.parsePacket();

  if (recvdPacketSize > 0) {

    static bool packet1 = true;
    if (packet1) {
      textDisplay("Ethernet connection established");
      packet1 = false;
    }

    Udp.read(recvdBuffer, UDP_TX_PACKET_MAX_SIZE);

    ethLastRecvd = millis();

    // Read thermocouples
    temps[0] = thermocouple01.readCelsius();
    temps[1] = thermocouple02.readCelsius();
    temps[2] = thermocouple03.readCelsius();
    temps[3] = thermocouple04.readCelsius();

    payloadStr = headerStr
                 + "," + seedOutputVal
                 + "," + BoosTAOutputVal
                 + "," + RepumpOutputVal
                 + "," + seedPower
                 + "," + BoosTAPower
                 + "," + RepumpPower;

    for (int i = 0; i < 4; i++) {
      if (isnan(temps[i])) {
        payloadStr = payloadStr + "," + "0.0";
      } else {
        payloadStr = payloadStr + "," + temps[i];
      }
    }

    payloadStr = payloadStr
                 + "," + String(currState[Shutter])
                 + "," + String(currState[Interlock])
                 + "," + String(state[Watchdog])
                 + "," + String(watchdogTripped)
                 + "," + String(currState[LasermetShutter])
                 + "," + String(currState[RepumpShutter]);

    Serial.println(payloadStr);
    Udp.beginPacket(IP_Collector, localPort);
    Udp.print(payloadStr);
    Udp.endPacket();

    memset(recvdBuffer, 0, sizeof(recvdBuffer));
  }
  ///////////////////////////////////////////////////////////////////////////////////////

  // UPDATE DISPLAY SCREEN //////////////////////////////////////////////////////////////
  if ((currentMillis - previousScreenUpdateMillis) >= screenUpdateInterval) { // TODO: OR if anything has been tripped OR button been pressed
    Serial.print("Sensor Value = ");
    Serial.print(seedOutputVal);
    Serial.print(" , Seed Power = ");
    Serial.println(seedPower);

    display.setCursor(0, 0);

    if (seedPower < seedPowerThresholdLower) {
      Serial.println("Seed Power Too Low!");
      display.println("Seed Power Too Low!");
    }
    else if (seedPower > seedPowerThresholdUpper) {
      Serial.println("Seed Power Too High!");
      display.println("Seed Power Too High!");
    } else {
      Serial.println("Seed Power is Fine");
      display.println("Seed Power is Fine");
    }

    display.setCursor(0, 8);
    display.print("Seed Power = ");
    display.println(seedPower);
    static int OLEDupdate = 0;
    String currmsg;
    if (OLEDupdate % 5 == 0) {
      currmsg = "BoosTA Power = " + String(BoosTAPower);
      textDisplay(currmsg);
      currmsg = "Repump Power = " + String(RepumpPower);
      textDisplay(currmsg);
      currmsg = "Lasermet = " + String(currState[LasermetShutter]);
      textDisplay(currmsg);
      currmsg = "Repump = " + String(currState[RepumpShutter]);
      textDisplay(currmsg);
    }
    OLEDupdate++;
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

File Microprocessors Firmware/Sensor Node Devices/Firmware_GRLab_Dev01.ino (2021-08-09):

/* Code for GRLab_Dev01 board

*/
#include <SPI.h>
#include <Ethernet.h>
#include<EthernetUdp.h>
#include "Adafruit_MAX31855.h"
//Needed for OLED
#include <Adafruit_SSD1306.h>
#include <Adafruit_GFX.h>

// OLED display TWI address /////////////////////////////////////////////////////////////////////////
#define OLED_ADDR   0x3C
// reset pin not used on 4-pin OLED module
Adafruit_SSD1306 display(-1);  // -1 = no reset pin

// Initialise Ethernet Parameters /////////////////////////////////////////////////////////////////////////
#define UDP_TX_PACKET_MAX_SIZE 150 //increase UDP size
EthernetUDP Udp;
byte mac[] = { 0xDE, 0xAD, 0xBE, 0xEF, 0xFE, 0xEB };
const unsigned int localPort = 1396;
IPAddress IP_Collector(169, 254, 128, 105);
IPAddress IP_GRLab_Dev01(169, 254, 128, 109);
char recvdBuffer[10];
int recvdPacketSize;
unsigned long ethLastRecvd = 0;
unsigned long ethTimeout = 40000;
///////////////////////////////////////////////////////////////////////////////////////////////////////////

// Initialise Variables ///////////////////////////////////////////////////////////////////////////////////
String headerStr = "GRLab,Dev01";
String payloadStr;
int sensorValueA0 = 0; // Analog input channel sensor ADC values
int sensorValueA1 = 0;
int sensorValueA2 = 0;
int sensorValueA3 = 0;
int sensorValueA4 = 0;
int sensorValueA5 = 0;

// Thermocouple Variables ////////////////////////////////////////////////////////////////////////////////
#define DO  2 // Common MOSI pin
#define CLK 3 // Common serial clock pin

// Chip select pins
#define CS01  4
#define CS02  5
#define CS03  6
#define CS04  7

// Button pin
#define buttonPin 47

//THERMOCOUPLES
Adafruit_MAX31855 thermocouple01(CLK, CS01, DO);
Adafruit_MAX31855 thermocouple02(CLK, CS02, DO);
Adafruit_MAX31855 thermocouple03(CLK, CS03, DO);
Adafruit_MAX31855 thermocouple04(CLK, CS04, DO);

double temps [4]; // Buffer to hold thermocouple data

int ledState = HIGH;         // the current state of the output pin
int buttonState;             // the current reading from the input pin
int lastButtonState = LOW;   // the previous reading from the input pin
unsigned long OLEDonms = 60000; // Screen on time in milliseconds
bool OLEDon = true;
bool updateOLED = false;

// the following variables are unsigned long's because the time, measured in miliseconds,
// will quickly become a bigger number than can be stored in an int.
unsigned long lastDebounceTime = 0;  // the last time the output pin was toggled
unsigned long debounceDelay = 50;    // the debounce time; increase if the output flickers
unsigned long lastButtonPress = 0; // This allows the screen to be on on start up



void setup() {

  // initialize and clear display
  display.begin(SSD1306_SWITCHCAPVCC, OLED_ADDR);
  display.clearDisplay();
  display.display();
  //display.dim(true);

  delay(1000); // Allow ethernet chip time to initialise after being powered up
  Serial.begin(57600);

  pinMode(53, OUTPUT); // Needed for slave select SPI for Mega (not connected)
  pinMode(10, OUTPUT); // SPI SS pin for most Arduino models (need to connect)
  pinMode(buttonPin, INPUT_PULLUP);

  Ethernet.begin(mac, IP_GRLab_Dev01);
  Udp.begin(localPort);
  delay(1000); // Allow ethernet chip time to initialise
  textDisplay("Ethernet initialisation started");
}
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
